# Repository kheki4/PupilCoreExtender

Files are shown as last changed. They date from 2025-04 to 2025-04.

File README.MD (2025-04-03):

# Camera arm extenders for the Pupil Core head-mounted eye-tracking glasses

***

PupilCoreExtender is a free and open-source SLS 3D printable extender bit alternative for the Pupil Core glasses, to allow more reliable eye-tracking with the device when its user frequently looks downwards.

This is a *non-profit and unofficial, hobby work*, compatible with the Core glasses of Pupil Labs.

Note: I use the device for pupillometry, so I have not thoroughly tested how my extenders change gaze tracking results, but certainly they improve a lot on pupil detection success and pupil data quality.

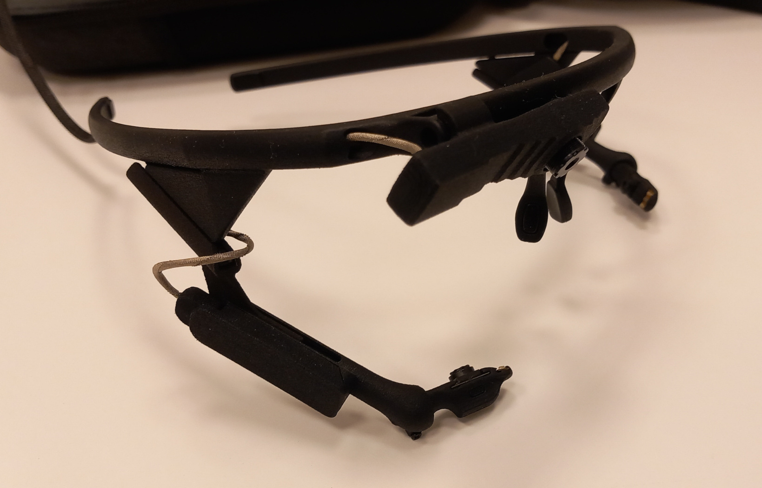
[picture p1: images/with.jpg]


***

## Introduction

Pupil Core is a cost effective head-mounted eye-tracking capable device, essentially consisting of two tiny NIR illuminators and two cameras, mounted on a blank frame, spiced with a world camera facing to the front.

If you are here owning no Pupil Core at the moment, you definitely need to first check out more recent products from Pupil Labs, as they already are more advanced than the Core, and I recommend buying them instead: https://pupil-labs.com

But if you have a Core and want to improve it, just continue reading on!

The company has released their newer products since the Core, like the Pupil Invisible and its successor Neon, which latter ones offer much more stability. However there are many Pupil Core glasses around the world, still in use or waiting to be used. Moreover, the Core is still (as of 2024 April) on the market officially.

The Pupil Core evidently suffers from a problem that the eye pupils easily get out of the reliable image area when the user looks downwards (e.g. looking on the ground while standing, or looking down on the desk top while sitting at a desk). The unadjustable nose-eyes-height and possible illumination inhomogenities also make it harder for the eye-tracking software to find the pupil and do its work.

The Pupil Core glasses by default come with a pair of orange-coloured extender bits. The point of these is to provide an alternative viewing angle and distance for the eye cameras to have a view on the eyes.

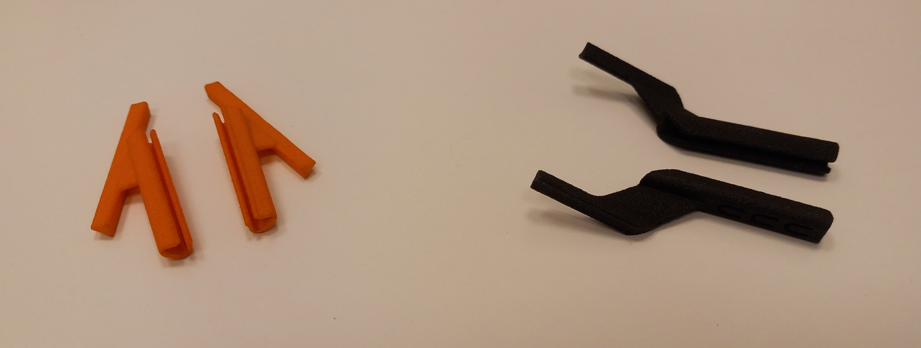
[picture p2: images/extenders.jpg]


As you might have tried to use the stock pair of extenders, you probably too have come to the conclusion that they could be optimized or improved. Partly because they introduce an angle both horizontally and vertically, but the vertical angle is too small to counteract the distance change from the eye introduced when attached to the frame, ultimately having only a very slight effective improvement relative to the state of the glasses when there are not extenders equipped at all. Also, the original extenders have sticking-out bits that could be spared/cut to optimize the occluded view to the user. To tackle these problems, I made my own extenders, that you can see here.

The below two pictures show a Core glasses device, in its default state, and the same glasses with my extenders equipped:

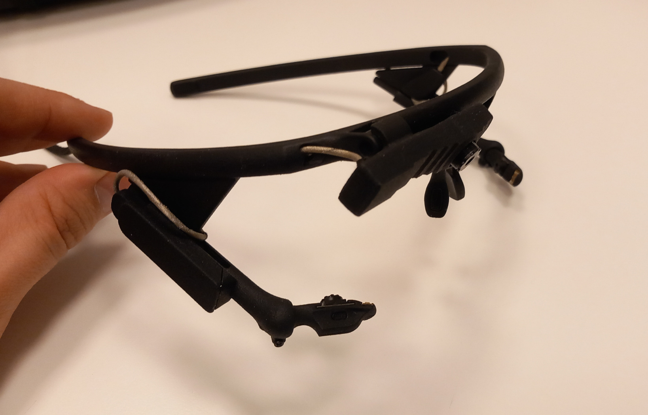
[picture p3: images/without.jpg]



These extenders can greatly reduce eyelash occlusion and improve pupil visibility for the cameras, if the person tends to look downwards while using the device, or if their nose-height relative to the eyes is different from typical. This is particularly useful for human factors studies, and studies where the material to be acted with, is partly placed on the desk top and the participants are sitting at it throughout the experiment.

The following two pair of screenshots show frames recorded from both eyes while the glasses was in its default state, with the user looking straight ahead to the monitor, and down on the computer keyboard:

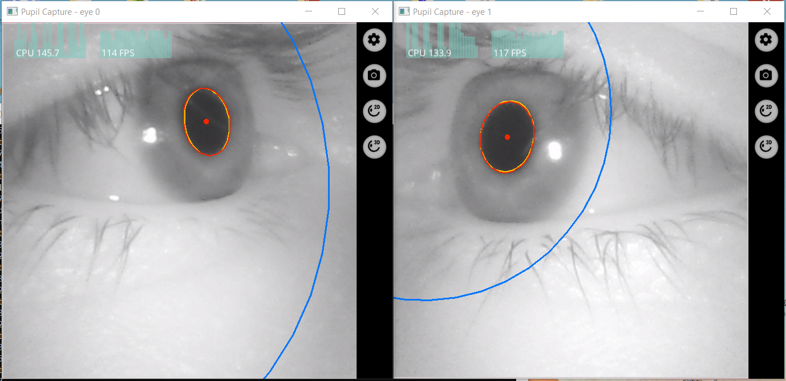
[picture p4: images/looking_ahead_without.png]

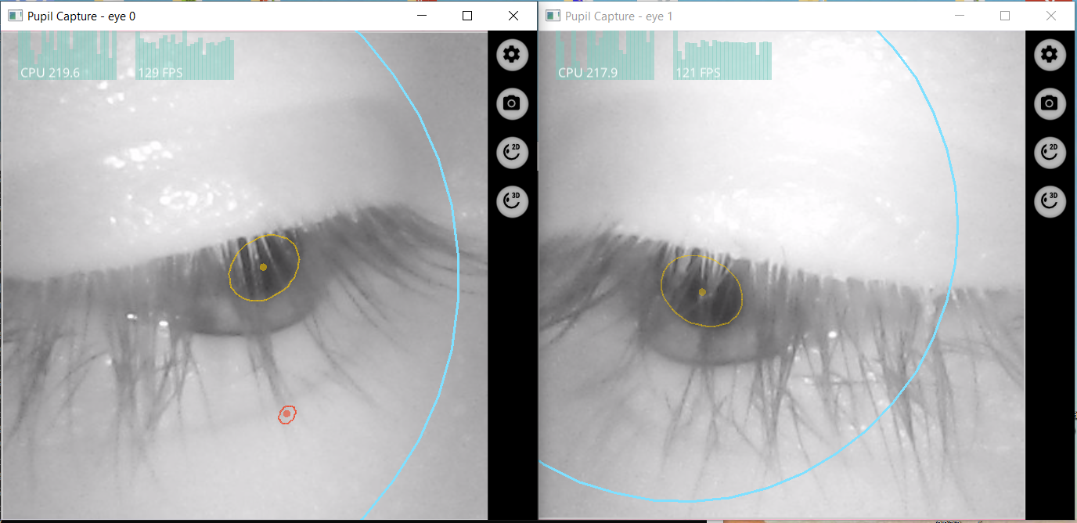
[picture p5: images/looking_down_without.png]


The following two pair of screenshots show frames recorded from both eyes, but with my extenders equipped. Again, with the user looking straight ahead to the monitor, and down on the computer keyboard:

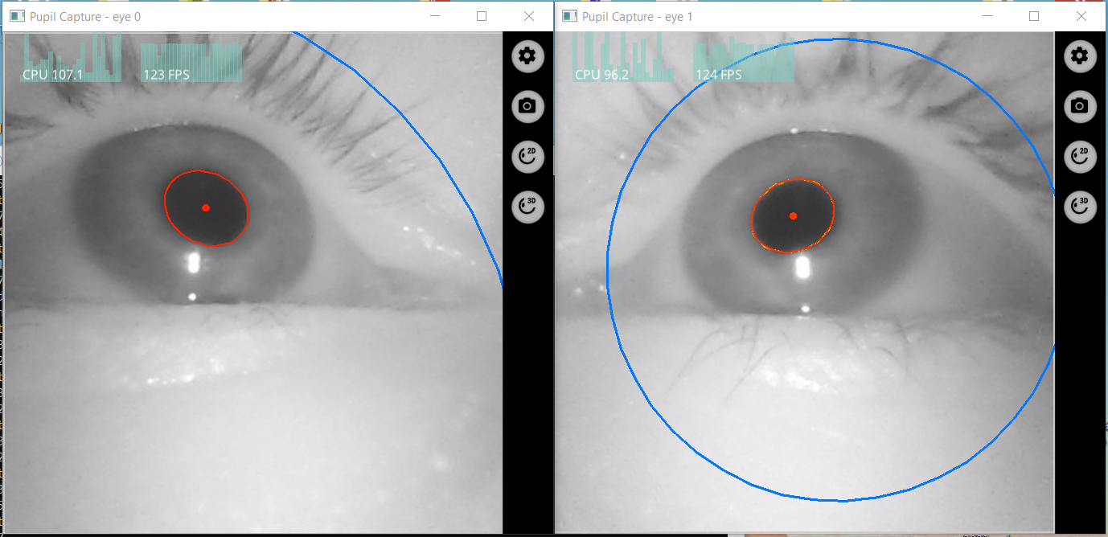
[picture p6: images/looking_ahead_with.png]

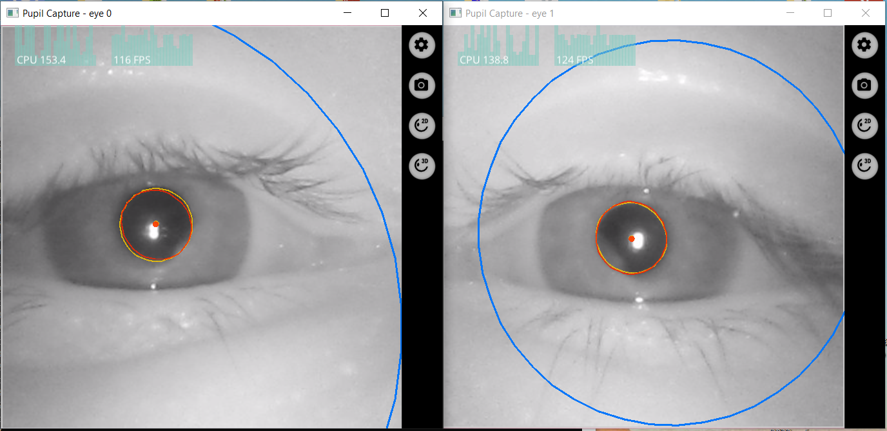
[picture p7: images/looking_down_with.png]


***

## The extender 3D models

You can just download the SLS-printable .STL files, and have them printed at any local 3D printing shop that has an SLS-machine, or have the bits ordered from JLCPCB or PCBWay for example, where they should cost no more than 1 USD each, plus VAT and shipping (as of 2025). There is a left and right version, symmetrical. There is no sanding or any additional surface finish needed on the 3D print, only the basic bead blasting that is anyway done by default at the manufacturer to remove leftover powder.

These are the models:

[Right side extender](https://raw.githubusercontent.com/kheki4/PupilCoreExtender/master/support_20deg_R.stl)

[Left side extender](https://raw.githubusercontent.com/kheki4/PupilCoreExtender/master/support_20deg_L.stl)

Imporantly, you need the bits made using stereolitography (SLS) printing, because they are so small, but at the same time need ample stiffness and resistance to mechanical stress, that SLS is highly optimal for producing them. (As you might have noticed, the original Pupil Core is also SLS-printed.)

After you have the bits printed, just slide them on the glasses rails and you are ready to go! 

For me this length was optimal, but if you find them too long, just gently cut off a little from either end, using a utility knife. The amount ultimately depends on your actual needs of typical looking directions. 

You can also find an editable model in the repository, which can be modified in Inventor, if you need so. (It produces a "R" variant when the mirror command at the end is added, and "L" if not added.)

***

## Additional note

Author: Gábor Bényei @ BUTE

License: CC BY-NC-SA

The 3D-printable models used here were created with Autodesk Inventor 2024. The models and any derivative work should be used for non-commercial, research/education purposes only.

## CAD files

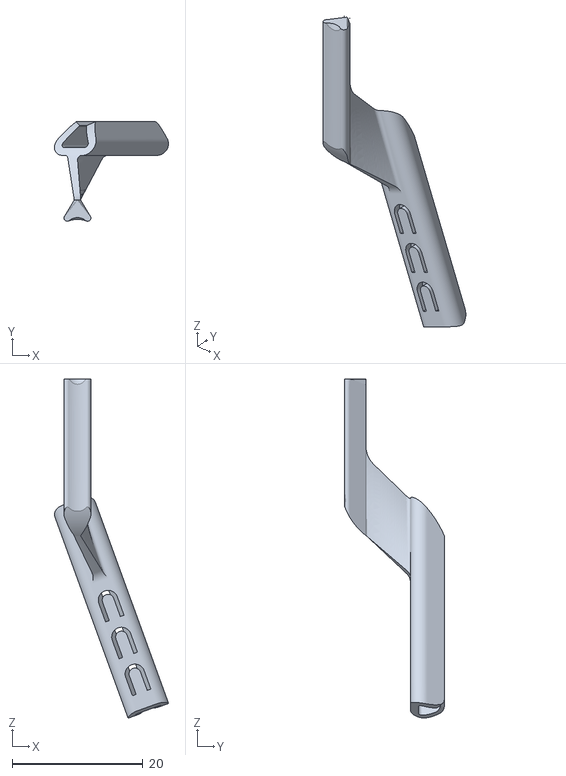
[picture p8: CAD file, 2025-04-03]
support_20deg_R.stl
17.4 x 15.2 x 51.8

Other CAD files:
support_20deg_L.stl
editable_models/support_20deg_RL.ipt
